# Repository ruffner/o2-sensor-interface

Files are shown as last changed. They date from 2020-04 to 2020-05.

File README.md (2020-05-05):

# o2-sensor-interface
An unconventional use of an [automotive oxygen sensor](https://www.oreillyauto.com/detail/b/bosch-3073/engine-sensors---emissions-25132/emission-smog-parts-16465/oxygen-air-fuel-ratio-sensor-12041/24932ed2a03f/bosch-oxygen-sensor/15510/2575736)

## Assembled Board
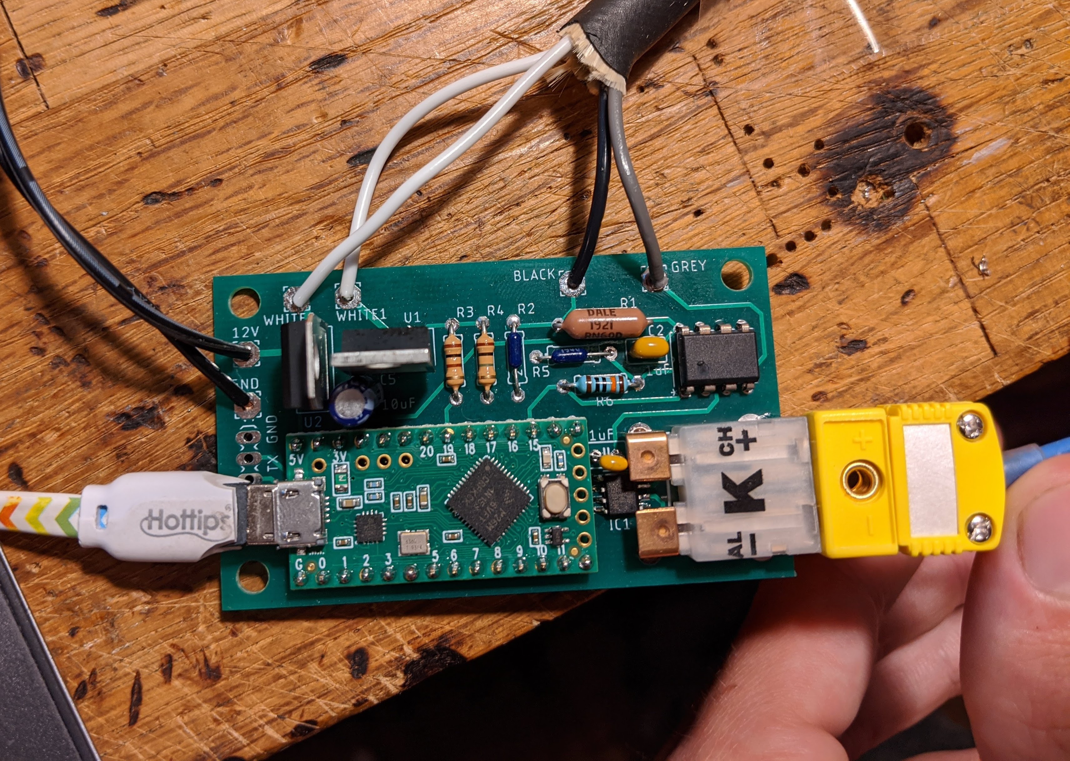
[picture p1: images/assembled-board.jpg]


## Software Setup
The board will emulate a USB serial com port. You can use the arduino serial monitor (Board -> Port menu). 
- [Arduino IDE 1.8.12](https://www.arduino.cc/en/main/software)

You can also use putty if on windows machine.
- [Putty](https://www.chiark.greenend.org.uk/~sgtatham/putty/latest.html)

You only need teensyduino to *update* code on the microcontroller. To simply monitor the serial output it is not needed.
- [TeensyDuino installer](https://www.pjrc.com/teensy/td_download.html)

Needed libs from the Arduino library manager
- Adafruit BusIO
- Adafruit MAX38155
- FIR Filter Arduino Library

## Schematic
Errata: 
- heater pin to mosfet should be 20 instead of 19 (for pwm capability). jumpered on board for now.
- 0.1uF cap across opamp input (grey wire). soldered on bottom of board for now.
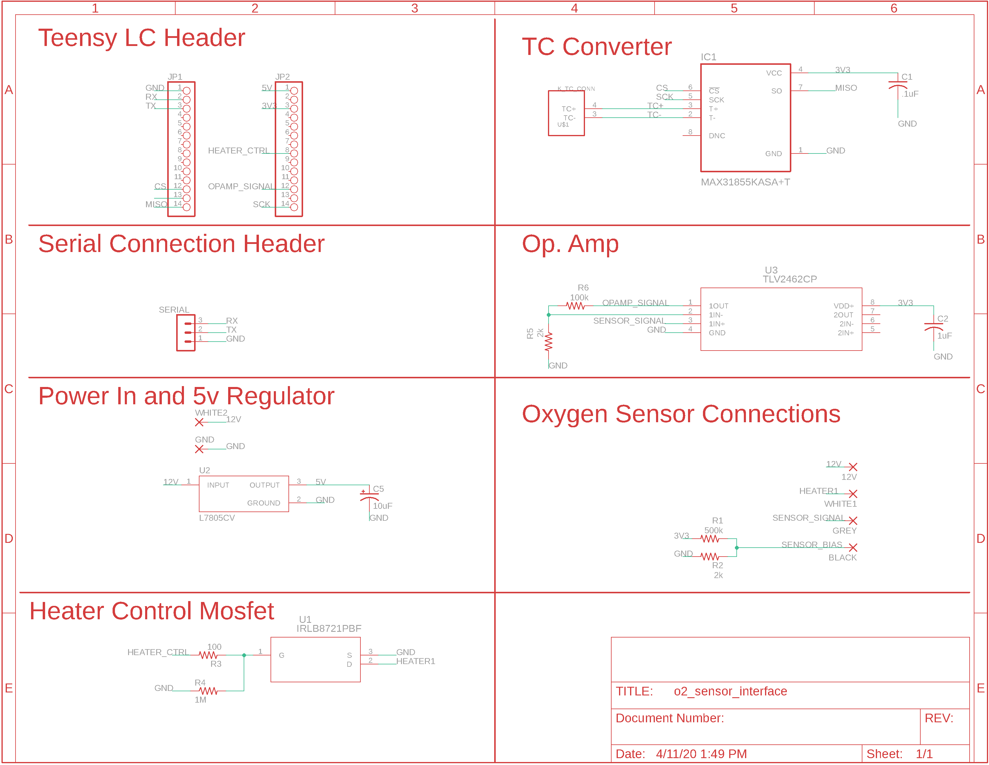
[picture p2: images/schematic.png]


## Layout
Dimensions in inches.

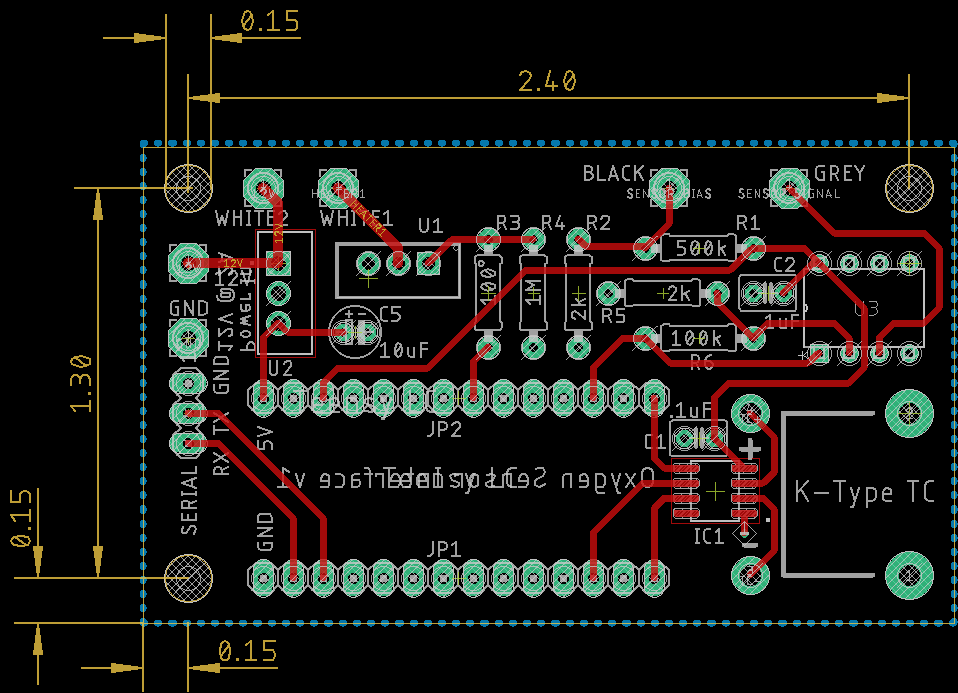
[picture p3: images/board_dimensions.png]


### Top Render
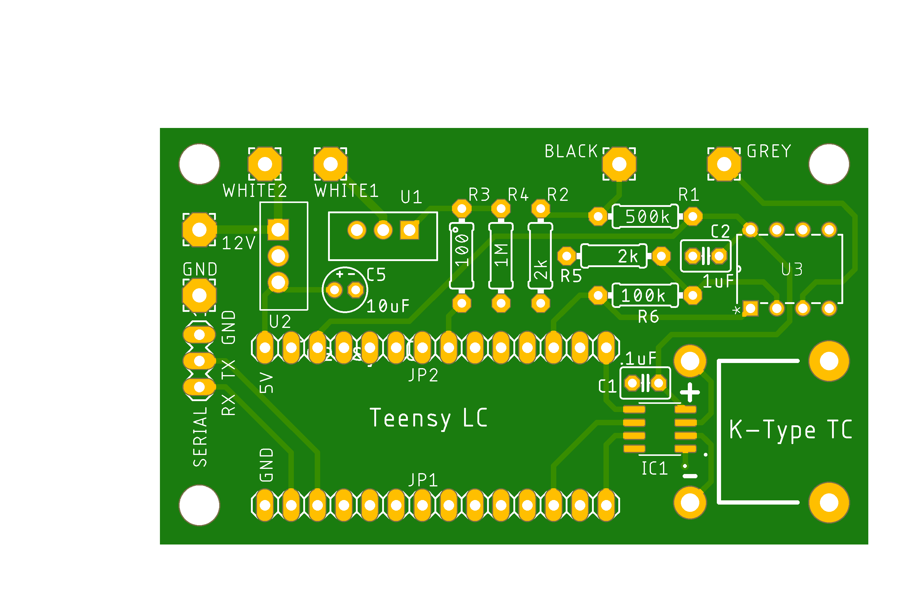
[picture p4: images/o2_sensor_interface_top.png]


### Bottom Render
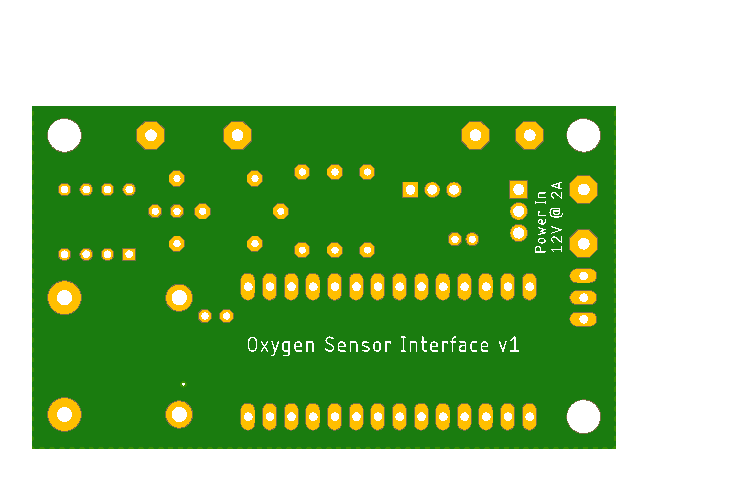
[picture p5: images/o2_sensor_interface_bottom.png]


## Partslist

Thermocouple: [https://www.amazon.com/gp/product/B07QK4ZG1G](https://www.amazon.com/gp/product/B07QK4ZG1G)

[Digikey BOM](pcb/Digikey_Bom_8219274.csv)

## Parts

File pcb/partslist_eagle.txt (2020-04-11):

Partlist

Exported from o2_sensor_interface.sch at 4/11/20 1:49 PM

EAGLE Version 9.5.1 Copyright (c) 1988-2019 Autodesk, Inc.

Assembly variant: 

Part     Value          Device          Package               Library        Sheet

12V                     3,17/1,3        3,17/1,3              wirepad        1
BLACK                   3,17/1,3        3,17/1,3              wirepad        1
C1       .1uF           C-US025-030X050 C025-030X050          adafruit       1
C2       1uF            C-US025-030X050 C025-030X050          adafruit       1
C5       10uF           CPOL-USE2-4     E2-4                  adafruit       1
GND                     3,17/1,3        3,17/1,3              wirepad        1
GREY                    3,17/1,3        3,17/1,3              wirepad        1
IC1      MAX31855KASA+T MAX31855KASA+T  SOIC127P600X175-8N    MAX31855KASA_T 1
JP1                     PINHD-1X14      1X14                  adafruit       1
JP2                     PINHD-1X14      1X14                  adafruit       1
R1       500k           R-US_0207/9     0207/9                adafruit       1
R2       2k             R-US_0207/9     0207/9                adafruit       1
R3       100            R-US_0207/9     0207/9                adafruit       1
R4       1M             R-US_0207/9     0207/9                adafruit       1
R5       2k             R-US_0207/9     0207/9                adafruit       1
R6       100k           R-US_0207/9     0207/9                adafruit       1
SERIAL                  MA03-1          MA03-1                con-lstb       1
U$1      K_TC_CONN      K_TC_CONN       TC_KTYPE              samdg          1
U1       IRLB8721PBF    IRLB8721PBF     PG-TO220-3            samdg          1
U2       L7805CV        L7805CV         TO255P1040X460X1968-3 L7805CV        1
U3       TLV2462CP      TLV2462CP       P8                    samdg          1
WHITE1                  3,17/1,3        3,17/1,3              wirepad        1
WHITE2                  3,17/1,3        3,17/1,3              wirepad        1

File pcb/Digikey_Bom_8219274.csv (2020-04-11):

Manufacturer Part Number | Manufacturer | Digi-Key Part Number | Customer Reference | Reference Designator | Packaging | Part Status | Quantity | Unit Price | Extended Price | Quantity Available | Mfg Std Lead Time | Description | RoHS Status | Lead Free Status | REACH Status
IRLB8721PBF | Infineon Technologies | IRLB8721PBF-ND |  |  | Tube | Active | 1 | 0.85000 | $0.85 | 3977 | 15 Weeks | MOSFET N-CH 30V 62A TO-220AB | ROHS3 Compliant | Lead free | REACH Unaffected
L7805CV | STMicroelectronics | 497-1443-5-ND |  |  | Tube | Active | 1 | 0.50000 | $0.50 | 28741 | 24 Weeks | IC REG LINEAR 5V 1.5A TO220AB | ROHS3 Compliant | Lead free | REACH Unaffected
DEV-13305 | SparkFun Electronics | 1568-1233-ND |  |  | Bulk | Active | 1 | 14.38000 | $14.38 | 448 | 8 Weeks | TEENSY-LC KL2X EVAL BRD | RoHS Compliant | Lead free | Not Available
TLV2462CP | Texas Instruments | 296-1892-5-ND |  |  | Tube | Active | 1 | 2.67000 | $2.67 | 436 | 12 Weeks | IC OPAMP GP 2 CIRCUIT 8DIP | ROHS3 Compliant | Lead free | REACH Unaffected
MAX31855KASA+T | Maxim Integrated | MAX31855KASA+TCT-ND |  |  | Cut Tape (CT) | Active | 1 | 5.31000 | $5.31 | 5138 | 13 Weeks | IC CONV THERMOCOUPLE-DGTL 8SOIC | ROHS3 Compliant | Lead free | REACH Unaffected
ECA-1VM100I | Panasonic Electronic Components | P19549CT-ND |  |  | Cut Tape (CT) | Active | 1 | 0.22000 | $0.22 | 9633 | 15 Weeks | CAP ALUM 10UF 20% 35V RADIAL | RoHS Compliant | Lead free | Not Available
C330C105K5R5TA7301 | KEMET | 399-9886-1-ND |  |  | Cut Tape (CT) | Active | 1 | 0.55000 | $0.55 | 50741 | 8 Weeks | CAP CER 1UF 50V X7R RADIAL | ROHS3 Compliant | Lead free | REACH Unaffected
C322C104K5R5TA7301 | KEMET | 399-9877-1-ND |  |  | Cut Tape (CT) | Active | 1 | 0.25000 | $0.25 | 89479 | 8 Weeks | CAP CER 0.1UF 50V X7R RADIAL | ROHS3 Compliant | Lead free | REACH Unaffected
CFR-25JB-52-100R | Yageo | 100QBK-ND |  |  | Bulk | Active | 1 | 0.10000 | $0.10 | 22187 | 16 Weeks | RES 100 OHM 1/4W 5% AXIAL | ROHS3 Compliant | Lead free | REACH Unaffected
CFR-25JB-52-1M | Yageo | 1.0MQBK-ND |  |  | Bulk | Active | 1 | 0.10000 | $0.10 | 39671 | 16 Weeks | RES 1M OHM 1/4W 5% AXIAL | ROHS3 Compliant | Lead free | REACH Unaffected
RN60D5003FB14 | Vishay Dale | 1135-1620-ND |  |  | Bulk | Active | 1 | 0.50000 | $0.50 | 767 | 34 Weeks | RES 500K OHM 1/4W 1% AXIAL | RoHS non-compliant | Contains lead | Not Available
CMF502K0000FHEB | Vishay Dale | CMF2.00KQFCT-ND |  |  | Cut Tape (CT) | Active | 2 | 0.67000 | $1.34 | 2373 | 12 Weeks | RES 2.00K OHM 1/4W 1% AXIAL | ROHS3 Compliant | Lead free | Not Available
RNF14FTD100K | Stackpole Electronics Inc | RNF14FTD100KCT-ND |  |  | Cut Tape (CT) | Active | 1 | 0.10000 | $0.10 | 78900 | 20 Weeks | RES 100K OHM 1/4W 1% AXIAL | ROHS3 Compliant | Lead free | REACH Unaffected
61301411121 | Würth Elektronik | 732-5325-ND |  |  | Bag | Active | 2 | 0.74000 | $1.48 | 5240 | 14 Weeks | CONN HEADER VERT 14POS 2.54MM | ROHS3 Compliant | Lead free | REACH Unaffected
PH1RB-03-UA | Adam Tech | 2057-PH1RB-03-UA-ND |  |  | Bag | Active | 1 | 0.11000 | $0.11 | 6527 | 9 Weeks | CONN HEADER R/A 3POS 2.54MM | ROHS3 Compliant | Lead free | Not Available
PRT-13612 | SparkFun Electronics | 1568-1306-ND |  |  | Bulk | Active | 1 | 4.38000 | $4.38 | 551 | 2 Weeks | THERMOCOUPLE CONN - PCC-SMP-K | RoHS Compliant | Lead free | Not Available

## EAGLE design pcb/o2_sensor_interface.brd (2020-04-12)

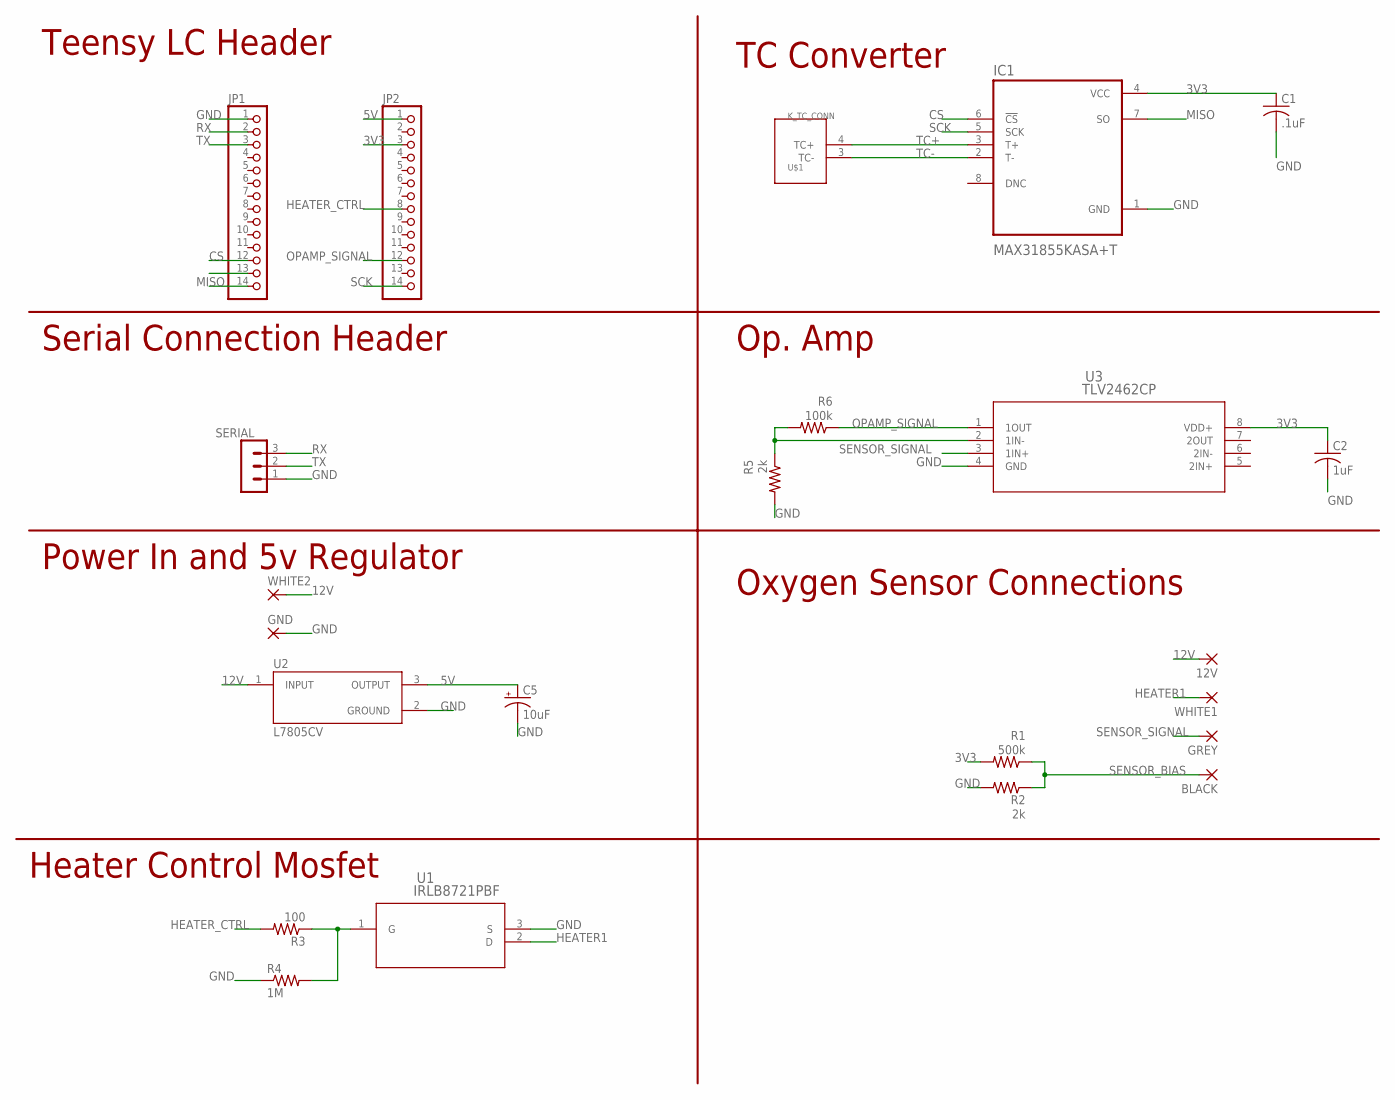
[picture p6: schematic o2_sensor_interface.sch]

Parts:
12V: 3,17/1,3
BLACK: 3,17/1,3
C1: .1uF; C025-030X050
C2: 1uF; C025-030X050
C5: 10uF; E2-4
GND: 3,17/1,3
GREY: 3,17/1,3
IC1: MAX31855KASA+T; SOIC127P600X175-8N
JP1, JP2: PINHD-1X14; 1X14
R1: 500k; 0207/9
R2, R5: 2k; 0207/9
R3: 100; 0207/9
R4: 1M; 0207/9
R6: 100k; 0207/9
SERIAL: MA03-1
U1: IRLB8721PBF; PG-TO220-3
U2: L7805CV; TO255P1040X460X1968-3
U3: TLV2462CP; P8
U$1: K_TC_CONN; TC_KTYPE
WHITE1, WHITE2: 3,17/1,3

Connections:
3V3: C1.1, C2.1, IC1.4 (VCC), JP2.3, R1.2, U3.8 (VDD+)
5V: C5.+, JP2.1, U2.3 (OUTPUT)
12V: 12V.1, U2.1 (INPUT), WHITE2.1
CS: IC1.6 (!CS), JP1.12
GND: C1.2, C2.2, C5.-, GND.1, IC1.1 (GND), JP1.1, R2.2, R4.1, R5.2, SERIAL.1, U1.3 (S), U2.2 (GROUND), U3.4 (GND)
HEATER1: U1.2 (D), WHITE1.1
HEATER_CTRL: JP2.8, R3.2
MISO: IC1.7 (SO), JP1.14
unnamed: R3.1, R4.2, U1.1 (G)
unnamed: R5.1, R6.2, U3.2 (1IN-)
OPAMP_SIGNAL: JP2.12, R6.1, U3.1 (1OUT)
RX: JP1.2, SERIAL.3
SCK: IC1.5 (SCK), JP2.14
SENSOR_BIAS: BLACK.1, R1.1, R2.1
SENSOR_SIGNAL: GREY.1, U3.3 (1IN+)
TC+: IC1.3 (T+), U$1.4 (TC+)
TC-: IC1.2 (T-), U$1.3 (TC-)
TX: JP1.3, SERIAL.2

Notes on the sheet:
Power In and 5v Regulator
Serial Connection Header
Oxygen Sensor Connections
Op. Amp
TC Converter
Teensy LC Header
Heater Control Mosfet

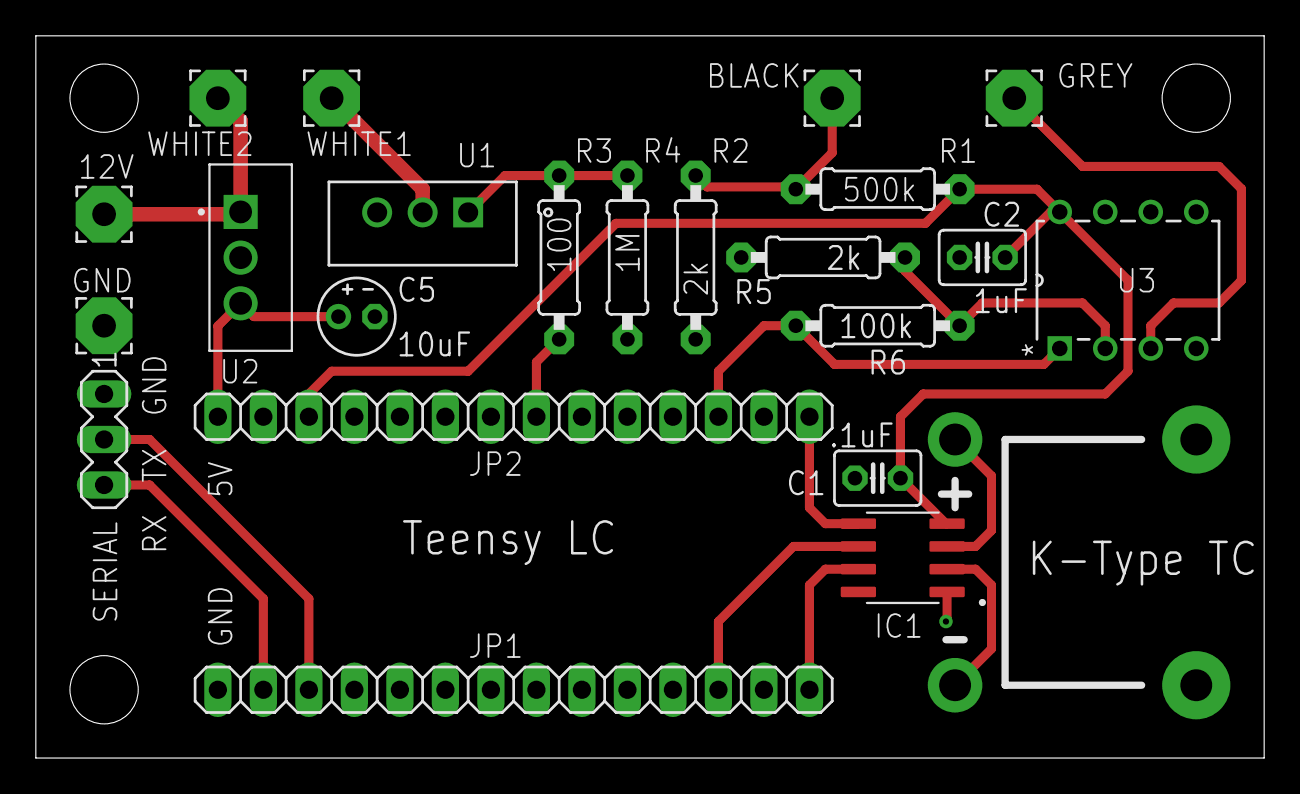
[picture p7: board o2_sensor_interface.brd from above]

Board: 2 copper layers, 68.6 x 40.3 mm, 23 parts (0 on the bottom side), 18 nets.

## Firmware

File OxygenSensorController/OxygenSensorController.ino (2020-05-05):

/*
  Read oxygen sensor output voltage from opamp and control oxygen sensor heater with
  PID control using a thermocouple.
  Log data serial as csv.
  Simple serial commands to control heater on/off and setpoint and logging on/off

  Matt Ruffner, April 2020
  https://github.com/ruffner/o2-sensor-interface
 */

#include <SPI.h>
#include <FIR.h>
#include "Adafruit_MAX31855.h"

#define SERIAL_BAUD     115200

#define ADC_REF         3.3
#define ADC_RES_INC     4095
#define ADC_RES_BITS    12

// this is the voltage applied to the black lead of the oxygen sensor
// V_bais = 3.3v * (2 kohm/502 kohm) volts
#define SENSOR_BIAS     0.01314741035 //volts

// non-inverting opamp gain 
// Gain = Vout / Vin 
//      = 1 + Rf/Rin 
//      = 1 + ( 100 kohm / 2 kohm )
#define OPAMP_GAIN      51

#define HEATER_PIN      20
#define ADC_PIN_OP_AMP  A1

// different intervals used. Log interval is the most useful to change.
#define COMMAND_CHECK_INTERVAL  50 // milliseconds
#define TC_UPDATE_INTERVAL      500
#define LOG_INTERVAL            4 // milliseconds

// create a thermocouple to digital interface over SPI
#define MAXIMUM_TC_TEMP         1000 // deg c
#define MAXCS   10
Adafruit_MAX31855 thermocouple(MAXCS);

// flag set in to trigger adc update 
volatile bool sampleUpdateFlag = false;

// last TC reading
double lastTCTemp = 0.0;

// heater pwm power
uint8_t heaterPwm = 200;

// sensor reading
float voltsOp = 0.0;

// lowpass filtered sensor reading
float voltsOpFilt = 0.0;

// change these if you want logging and/or heating to start immediately upon startup
bool loggingActive = true;
bool heating = true;

// timestamp holders
unsigned long lastCommandCheck, lastHeaterUpdate, lastLogTime;
unsigned long lastTCUpdate=0;

IntervalTimer sampleTimer;

FIR<float, 13> lpfilt;

//////////////////////////////////////////////////////////////////////////////////////////
// callback for adc sample timer
void setSampleUpdateFlag() {
  sampleUpdateFlag = true;
}

//////////////////////////////////////////////////////////////////////////////////////////
// store TC temp reading in deg celcius
void updateTC() {
   double c = thermocouple.readCelsius();
   if (isnan(c)) {
     //Serial.println("Something wrong with thermocouple!");
     //lastTCTemp = 0;
   } else {
     lastTCTemp = c;
   }
}


//////////////////////////////////////////////////////////////////////////////////////////
// parse simple command strings
// log <on/off>: turn serial csv output on/off
//    heater <on/off>: turn relay toggle pin for heating element on/off
//    heater period <1-2^16>: in milliseconds, the period of the 50% duty cycle toggle pin
void checkForCommand() {
  if( Serial.available() ){
    String cmd = Serial.readStringUntil('\n');
    cmd.trim();
    
    if( cmd.length() == 0 ) return;

    int ind1 = cmd.indexOf(' ');  //finds location of first space
    if( ind1 == -1 ) return;
    String op1 = cmd.substring(0, ind1);   //captures first data String
    
    int ind2 = cmd.indexOf(' ', ind1+1 );   //finds location of second space
    if( ind2 == -1 ){
      ind2 = cmd.length()-1;
    }
    String op2 = cmd.substring(ind1+1, ind2+1);   //captures second data String;  
    int ind3 = cmd.indexOf(' ', ind2+1 );
    String op3;
    if( ind3 < 0 ){
      ind3 = cmd.length()-1;
    }
    op3 = cmd.substring(ind2+1, ind3+1);

    if( op1.toLowerCase().equals("log") ){
      if( op2.toLowerCase().equals("on") ){
        loggingActive = true;
      } else if( op2.toLowerCase().equals("off") ){
        loggingActive = false;
      }
    } else if( op1.toLowerCase().startsWith("heater") ){
      if( op2.toLowerCase().startsWith("on") ){
        heating = true;
        if( op3.length() > 0 ){
          heaterPwm = min(max(op3.toInt(), 0), 255);
          analogWrite(HEATER_PIN, heaterPwm);
        }
      } else if( op2.toLowerCase().startsWith("off") ){
        heating = false;
        heaterPwm = 0;
        analogWrite(HEATER_PIN, 0);
      }
    } 
  }
}


//////////////////////////////////////////////////////////////////////////////////////////
// rescale adc reading to volts, taking into account opamp gain and adc 
// resolution
float rescaleToVolts(unsigned int raw) {
  return ((float)(raw) / (float)ADC_RES_INC)*(float)ADC_REF/(float)OPAMP_GAIN;
}


//////////////////////////////////////////////////////////////////////////////////////////
// setup serial gpio etc
void setup() {
  // initialize the digital pin as an output.
  pinMode(HEATER_PIN, OUTPUT);
  pinMode(ADC_PIN_OP_AMP, INPUT);
  
  Serial.begin(SERIAL_BAUD);

  // low pass with 1Hz cutoff freq
  float coeffs[33] = {
    0.0044,
    0.0050,
    0.0065,
    0.0089,
    0.0122,
    0.0162,
    0.0208,
    0.0258,
    0.0310,
    0.0362,
    0.0413,
    0.0460,
    0.0501,
    0.0534,
    0.0559,
    0.0575,
    0.0580,
    0.0575,
    0.0559,
    0.0534,
    0.0501,
    0.0460,
    0.0413,
    0.0362,
    0.0310,
    0.0258,
    0.0208,
    0.0162,
    0.0122,
    0.0089,
    0.0065,
    0.0050,
    0.0044};

  lpfilt.setFilterCoeffs(coeffs);
  Serial.print("Low Pass Filter Gain: ");
  Serial.println(lpfilt.getGain());

  // 0-4095
  analogReadResolution(ADC_RES_BITS);
  
  // hardware average 64 samples
  analogReadAveraging(64);

  sampleTimer.begin(setSampleUpdateFlag, LOG_INTERVAL*1000);
  
  delay(1000);

  analogWrite(HEATER_PIN, heaterPwm);
}


//////////////////////////////////////////////////////////////////////////////////////////
// main loop foeva
void loop() {
  unsigned long now = millis();

  if( now - lastTCUpdate > TC_UPDATE_INTERVAL ){
    lastTCUpdate = now;
    updateTC();
  }
  
  if( now - lastCommandCheck > COMMAND_CHECK_INTERVAL ){
    lastCommandCheck = now;
    checkForCommand();
  }

  if( sampleUpdateFlag ){
    unsigned int rawOp = analogRead(ADC_PIN_OP_AMP);
    voltsOp  = (rescaleToVolts(rawOp));
    voltsOpFilt = lpfilt.processReading(voltsOp);
    sampleUpdateFlag = false;
  }

  if( !loggingActive ) return;

  if( now - lastLogTime > LOG_INTERVAL ){
  //if( now - lastLogTime > LOG_INTERVAL && heaterStatus == 1 ){  
    lastLogTime = now;
  
    Serial.print(now);
    Serial.print(",");
    Serial.print(heaterPwm);
    Serial.print(",");
    Serial.print(voltsOp, DEC);
    Serial.print(",");
    Serial.print(voltsOpFilt, DEC);
    Serial.print(",");
    Serial.println(lastTCTemp,DEC);
  }
}

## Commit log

2020-04-11 initial work on interface board.
    [Digikey_Bom_8219274.csv, o2_sensor_interface.brd, o2_sensor_interface.sch]
2020-04-11 updated bom to include male headers for teensy
    [Digikey_Bom_8219274.csv]
2020-04-11 added tc connection socket
    [Digikey_Bom_8219274.csv, o2_sensor_interface.brd, o2_sensor_interface.sch]
2020-04-12 silkscreen edit and camfile upload
    [o2_sensor_interface.brd]
2020-04-20 added arduino control code and pic of assembled board
2020-04-27 test data and fixed power firmware
    [no_o2_test.csv, no_o2_test2.csv, no_o2_test2_output.csv, no_o2_test_output.csv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]
2020-05-05 increase sample rate to 200Hz and add 33 tap fir lowpass to output

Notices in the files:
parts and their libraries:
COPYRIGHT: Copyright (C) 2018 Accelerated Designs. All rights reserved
